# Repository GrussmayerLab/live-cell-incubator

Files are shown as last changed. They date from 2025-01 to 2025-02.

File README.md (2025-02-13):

This repository is created for an open-hardware project to develop a [live cell imaging incubator](https://grussmayerlab.github.io/live-cell-incubator/) by the KG group at TU Delft.

## Licensing and Attribution

This repository is licensed under the [MIT License]. You are generally free to reuse or extend upon this code as you see fit; just include the original copy of the license (which is preserved when you "make a template"). While it's not necessary, we'd love to hear from you if you do use this template, and how we can improve it for future use!

The deployment GitHub Actions workflow is heavily based on GitHub's mixed-party [starter workflows]. A copy of their MIT License is available in [actions/starter-workflows].

----

[MIT License]: https://en.wikipedia.org/wiki/MIT_License
[starter workflows]: https://github.com/actions/starter-workflows/blob/main/pages/jekyll.yml
[actions/starter-workflows]: https://github.com/actions/starter-workflows/blob/main/LICENSE

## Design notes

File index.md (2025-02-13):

---
title: Home
layout: home
---

# RM21Blanket - a live cell incubator 
 
Live cell experiments have become routine in the past decade or so and thus, a well-documented, (easy to adapt) open-source incubator design will be helpful to the life sciences community.

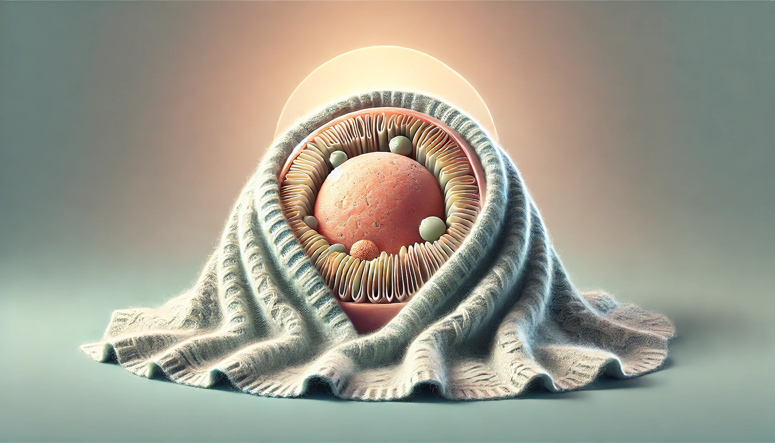
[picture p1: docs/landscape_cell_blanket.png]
A cell with a blanket alt >


In this project we have developed a live cell incubator with environmental controls for our home-built microscope based on the [RM21 platform by Mad City Labs](https://www.madcitylabs.com/rm21.html). This was the second iteration of our incubator chamber as the first version faced certain leakage and robustness issues. Our current design addresses these issues and incorporates several key features of an "ideal" incubator for live cell imaging:

1. Precise temperature control: Maintains a stable temperature, typically around 37°C for mammalian cells, with minimal fluctuations using commercial Oko Lab temperature control units.
2. Gas control: Accurate CO2 regulation (typically 5%) using Oko Lab CO2 control units, ensuring a consistent atmospheric environment.
3. Optimized flow dynamics: Careful consideration given to the flow and distribution of hot air and CO2 within the chamber for uniform environmental conditions.
4. Minimal evaporation and condensation: Use of closed ibidi dishes or sealed chambers significantly reduces these issues.
5. Compatibility: Designed for easy installation and compatibility with our home-built microscope setup.
6. Data logging: Utilizes Oko Lab control monitor for recording environmental parameters.
7. Multiple channel control: Ability to control temperature and CO2 parameters simultaneously for precise environmental regulation.
8. Minimal disturbance: Design allows for long-term imaging with minimal interference to the sample.
9. Design and Material choices: Black non-translucent PMMA material was chosen to fabricate the chamber based on its temperature tolerance, and also to avoid instances of stray light. The chamber has a door for easy mounting and access to the sample. Two sets of the door have been fabricated and can be easily interchanged- one with a transparent PMMA and one with the black non-translucent PMMA. For experiments involving microfluidic devices or specialized culture platforms, a transparent door allows researchers to easily check for issues like air bubbles, media evaporation, or unexpected cell behavior without compromising the experimental conditions.

While our current design doesn't include active humidity control or O2 regulation, the sealed environment and optimized flow dynamics help maintain stable conditions suitable for most standard cell culture experiments.

# Current State of the Project
Our live cell incubator project has successfully completed its second iteration, addressing leakage and robustness issues from the first version. 

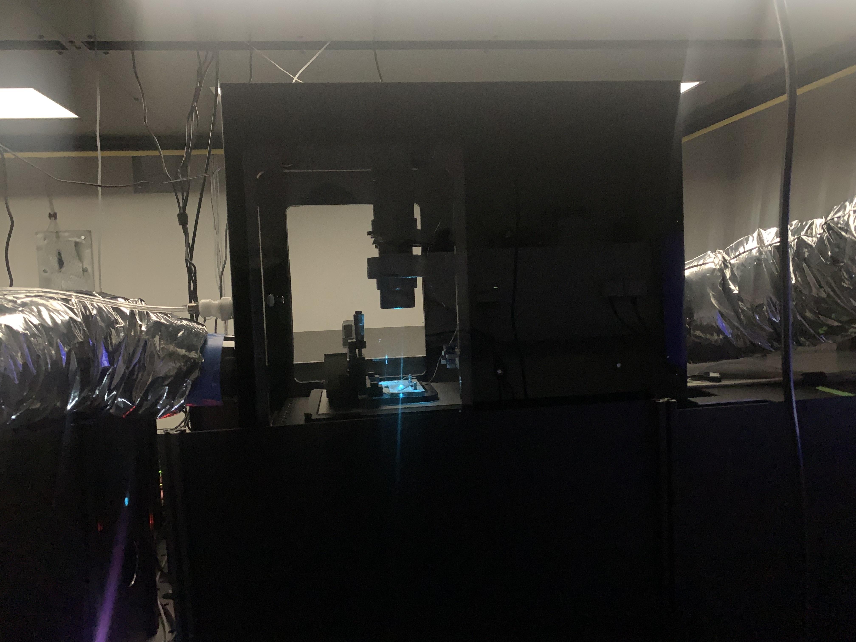
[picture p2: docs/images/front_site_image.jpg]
<br><br>

All the technical drawings, design files and bill of materials for the current version are available in the [project repo](https://github.com/GrussmayerLab/live-cell-incubator/). You can find the detailed [build instructions here]({{site.baseurl}}/build_instructions.html). Other than the mechanical parts listed in the BOM required to manufacture the chamber, you will also need:<br><br>

| Item| Quantity | Product Link| |
|----------|----------|---------|----|
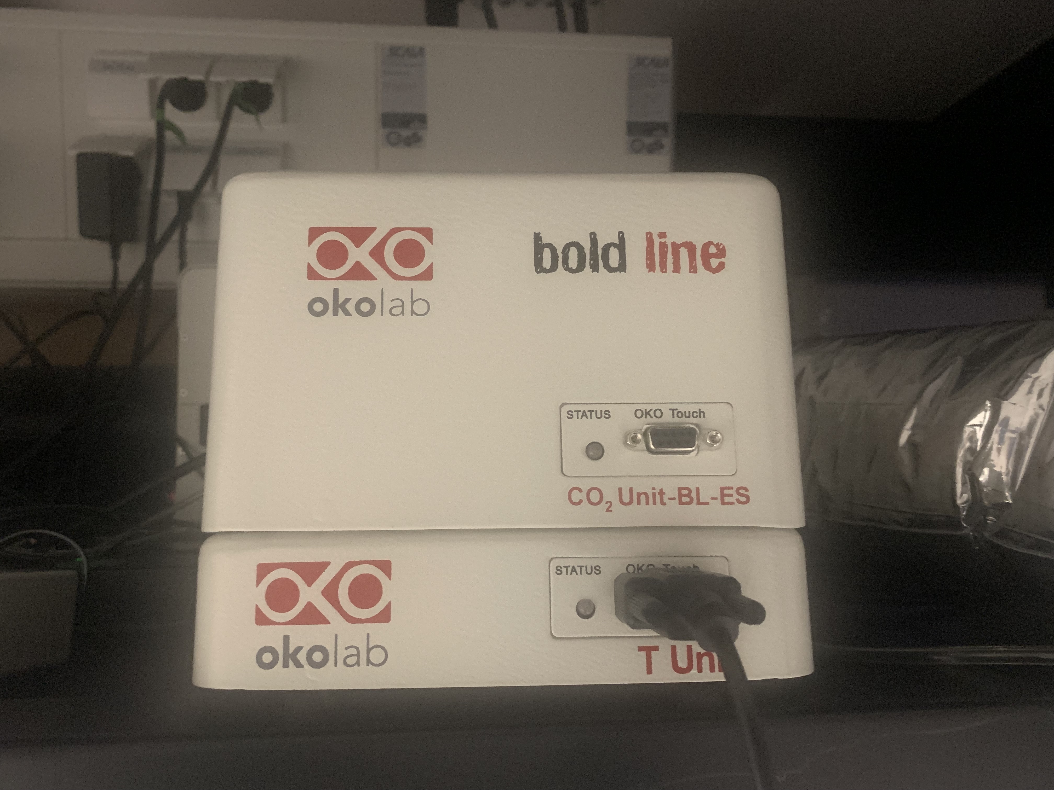
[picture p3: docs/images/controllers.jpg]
| Temperature control unit from Oko Lab with a chamber temperature sensor and a sample temperature sensor  | 1  | https://www.oko-lab.com/live-cell-imaging/cage-incubator/temperature-unit |   |
| CO2 control unit from Oko Lab  | 1   | https://www.oko-lab.com/gas-mixing/for-microscope-incubators/co2-unit-bl |  
| CO2 sensor   | 1  | | |
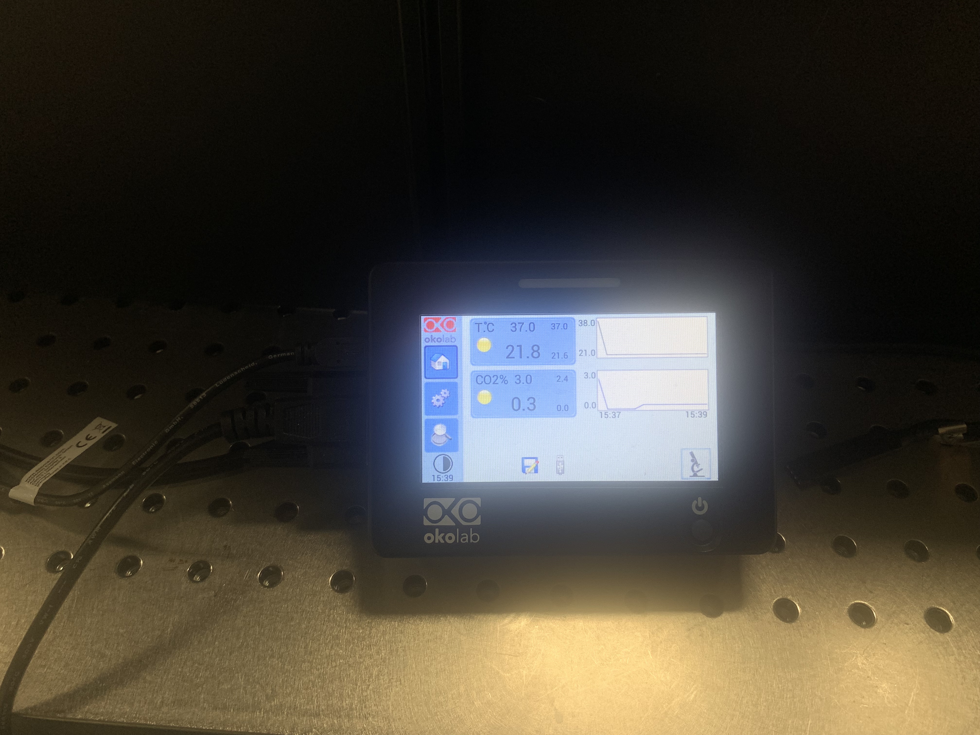
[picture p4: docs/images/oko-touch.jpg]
| Touch screen interface unit from Oko Lab  | 1  | https://okolab4microsystems.com/okolab_codes/oko-touch/ | 
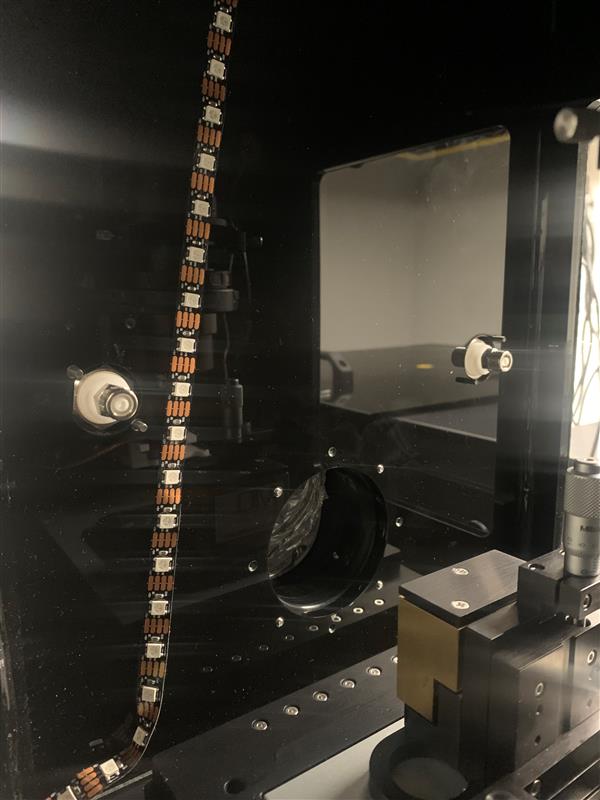
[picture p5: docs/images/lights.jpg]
| LED strip lights (optional)   | 1m  | Generic |  

# Testing and Validation
The incubator has been tested and is able to maintain contant temperature and CO2 levels for 4+ hours. We haven't tested extended durations yet as we do not currently image live cells for longer durations. A cell viability assay post imaging for 4 hours with the incubator resulted in only about 6-8% decline in viability.

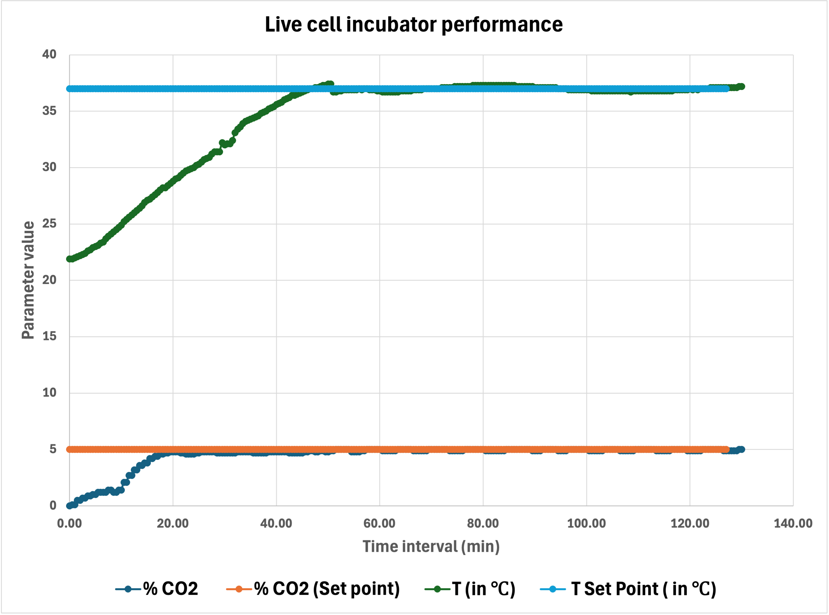
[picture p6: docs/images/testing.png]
<br><br>

# Future Plans
An active point of focus with respect to this design is to minimize environmental fluctuations while exchanging samples during imaging. The chamber door in our current design is relatively large which might mean everytime the door is opened, there could be sudden sharp fluctuations in the chamber equilibrium. In our testing, however, these effects weren't significant and the equilibrium is quickly maintained again. This could be because of the position of the gas inlet and outlet points with respect to the position of the door. Nevertheless, it is always advisable to go for a smaller door whenever possible. The incubator chamber can also be of a smaller footprint if it is designed just for fluorescence imaging and therefore, need not enclose the Koehler lamp as it does in the current design. 

Although not necessary at this point of time for our work, there is the option of exploring active humidity control for the incubator, if needed for specific experiments. This would also entail the issue of condensation which could potentially damage the optomechanics housed within the incubator chamber, so considerations have to be made accordingly. Additionally, for experiments requiring strictly hypoxic conditions, an active O2 control would be a good choice.

# Getting Started and Project Support
The information provided on this page should be sufficient for anyone looking to build a live cell incubator for imaging experiments for their microscope. Please report any questions or even suggestions you might have for us, using the "Issues" tab on our [github repo](https://github.com/GrussmayerLab/live-cell-incubator/issues) for this project. 

# License Information

# Special Thanks
This project was funded by the Open Hardware Stimulation Fund of the [Delft Open Hardware initiative](https://www.tudelft.nl/open-hardware/about-us). The chamber was designed by Frank Schilder and Moritz Engelhardt and developed by Frank, Moritz, and  Niek van Zon from TU Delft.

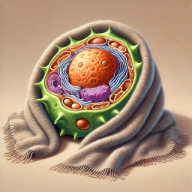
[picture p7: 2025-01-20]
docs/android-chrome-192x192.png

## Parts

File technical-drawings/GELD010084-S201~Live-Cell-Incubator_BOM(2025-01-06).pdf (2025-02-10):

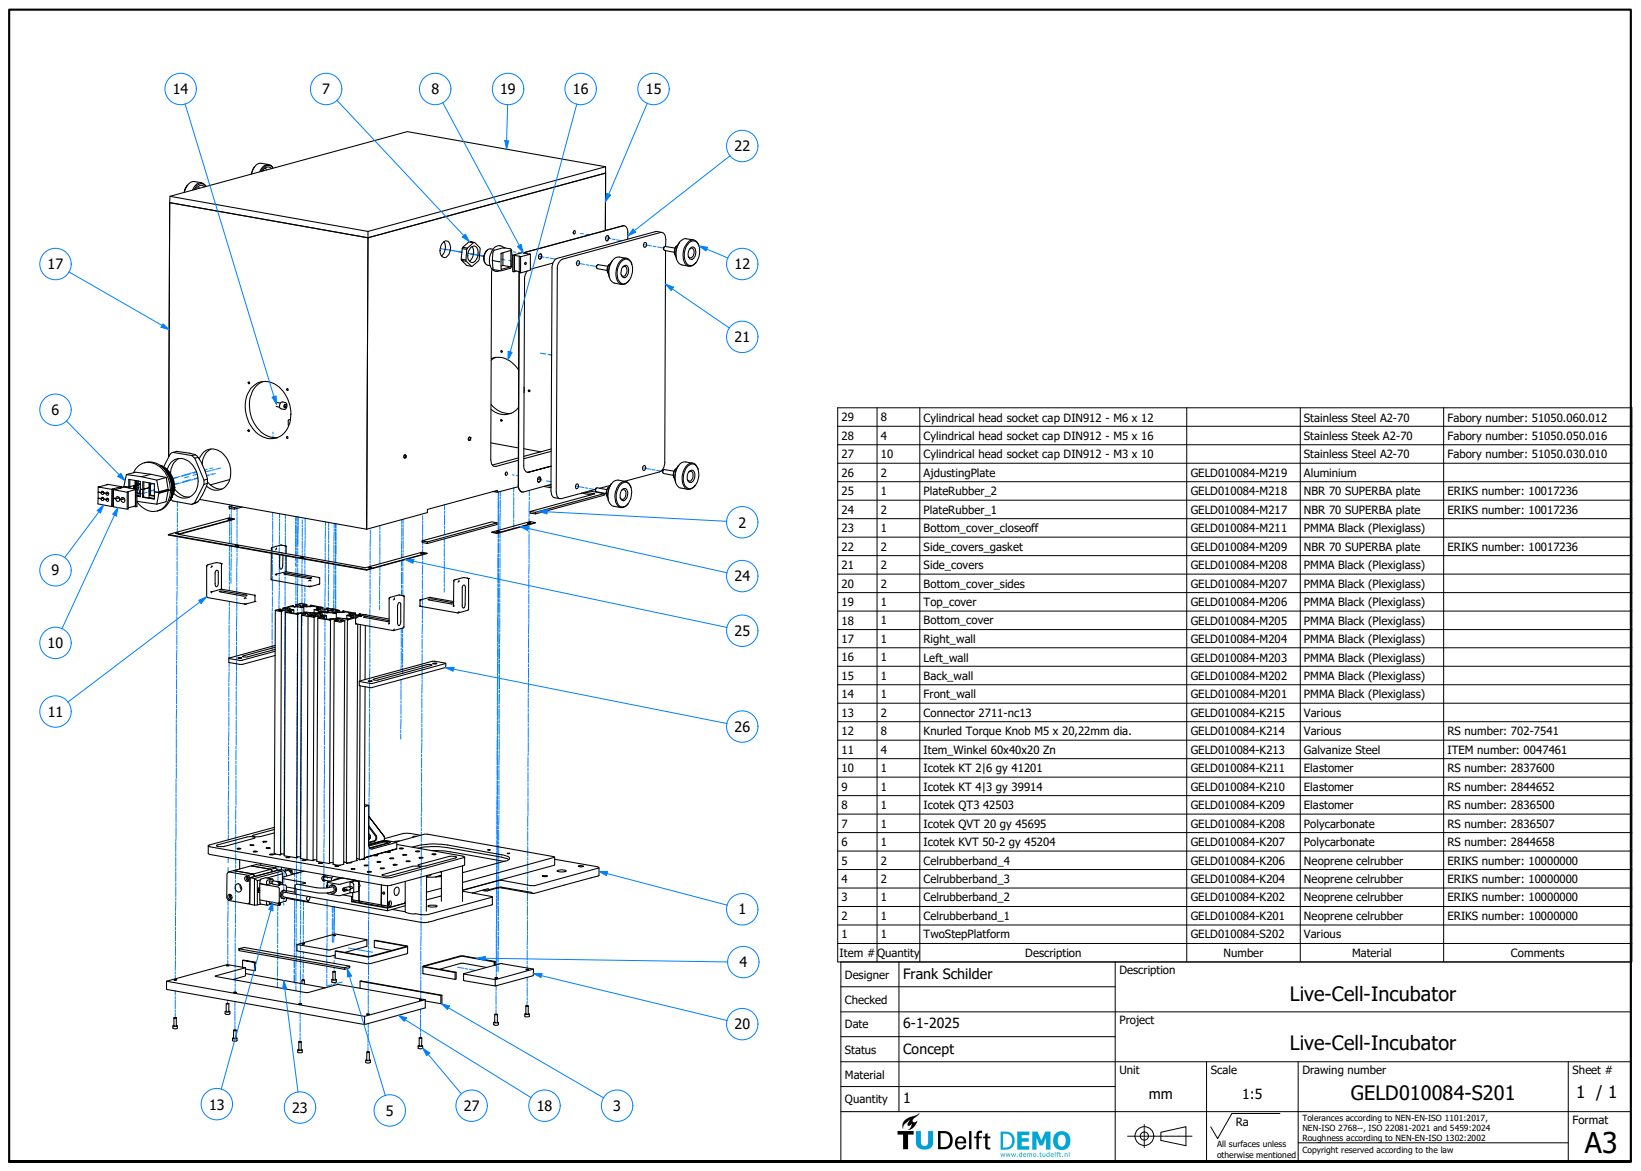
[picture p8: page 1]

29 | 8 | Cylindrical head socket cap DIN912 - M6 x 12 | | Stainless Steel A2-70 | Fabory number: 51050.060.012
28 | 4 | Cylindrical head socket cap DIN912 - M5 x 16 | | Stainless Steek A2-70 | Fabory number: 51050.050.016
27 | 10 | Cylindrical head socket cap DIN912 - M3 x 10 | | Stainless Steel A2-70 | Fabory number: 51050.030.010
26 | 2 | AjdustingPlate | GELD010084-M219 | Aluminium
25 | 1 | PlateRubber_2 | GELD010084-M218 | NBR 70 SUPERBA plate | ERIKS number: 10017236
24 | 2 | PlateRubber_1 | GELD010084-M217 | NBR 70 SUPERBA plate | ERIKS number: 10017236
23 | 1 | Bottom_cover_closeoff | GELD010084-M211 | PMMA Black (Plexiglass)
22 | 2 | Side_covers_gasket | GELD010084-M209 | NBR 70 SUPERBA plate | ERIKS number: 10017236
21 | 2 | Side_covers | GELD010084-M208 | PMMA Black (Plexiglass)
20 | 2 | Bottom_cover_sides | GELD010084-M207 | PMMA Black (Plexiglass)
19 | 1 | Top_cover | GELD010084-M206 | PMMA Black (Plexiglass)
18 | 1 | Bottom_cover | GELD010084-M205 | PMMA Black (Plexiglass)
17 | 1 | Right_wall | GELD010084-M204 | PMMA Black (Plexiglass)
16 | 1 | Left_wall | GELD010084-M203 | PMMA Black (Plexiglass)
15 | 1 | Back_wall | GELD010084-M202 | PMMA Black (Plexiglass)
14 | 1 | Front_wall | GELD010084-M201 | PMMA Black (Plexiglass)
13 | 2 | Connector 2711-nc13 | GELD010084-K215 | Various
12 | 8 | Knurled Torque Knob M5 x 20,22mm dia. | GELD010084-K214 | Various | RS number: 702-7541
11 | 4 | Item_Winkel 60x40x20 Zn | GELD010084-K213 | Galvanize Steel | ITEM number: 0047461
10 | 1 | Icotek KT 2|6 gy 41201 | GELD010084-K211 | Elastomer | RS number: 2837600
9 | 1 | Icotek KT 4|3 gy 39914 | GELD010084-K210 | Elastomer | RS number: 2844652
8 | 1 | Icotek QT3 42503 | GELD010084-K209 | Elastomer | RS number: 2836500
7 | 1 | Icotek QVT 20 gy 45695 | GELD010084-K208 | Polycarbonate | RS number: 2836507
6 | 1 | Icotek KVT 50-2 gy 45204 | GELD010084-K207 | Polycarbonate | RS number: 2844658
5 | 2 | Celrubberband_4 | GELD010084-K206 | Neoprene celrubber | ERIKS number: 10000000
4 | 2 | Celrubberband_3 | GELD010084-K204 | Neoprene celrubber | ERIKS number: 10000000
3 | 1 | Celrubberband_2 | GELD010084-K202 | Neoprene celrubber | ERIKS number: 10000000
2 | 1 | Celrubberband_1 | GELD010084-K201 | Neoprene celrubber | ERIKS number: 10000000
1 | 1 | TwoStepPlatform | GELD010084-S202 | Various
Item # Quantity | | Description | Number | Material | Comments
Designer | Frank Schilder | Description Live-Cell-Incubator

Checked
Date | 6-1-2025 | Project Live-Cell-Incubator

Status | Concept

Material | | Unit mm | Scale 1:5 | Drawing number GELD010084-S201 | Sheet # 1 / 1

Quantity | 1

Ra All surfaces unless otherwise mentioned | Tolerances according to NEN-EN-ISO 1101:2017, NEN-ISO 2768--, ISO 22081-2021 and 5459:2024 Roughness according to NEN-EN-ISO 1302:2002 | Format A3

Copyright reserved according to the law

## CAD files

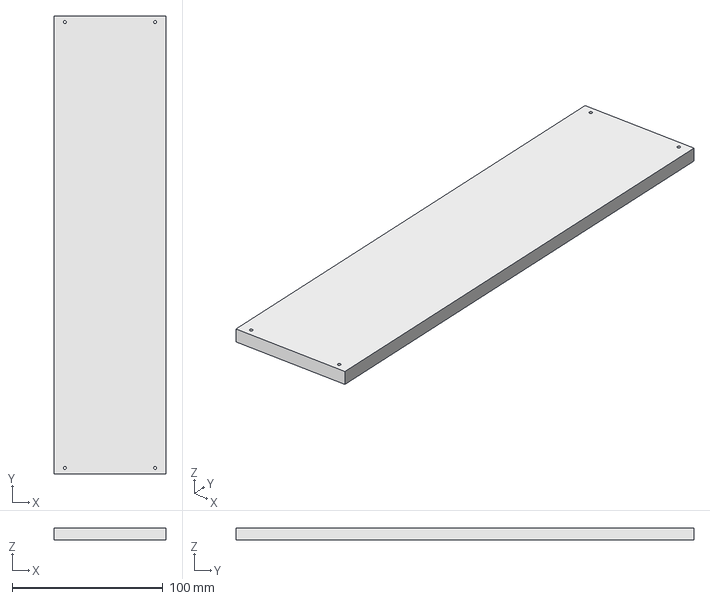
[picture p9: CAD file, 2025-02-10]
technical-drawings/GELD010084-M215~Drill_guide1(2024-12-31).stp
74.2 x 304.1 x 8.00 mm

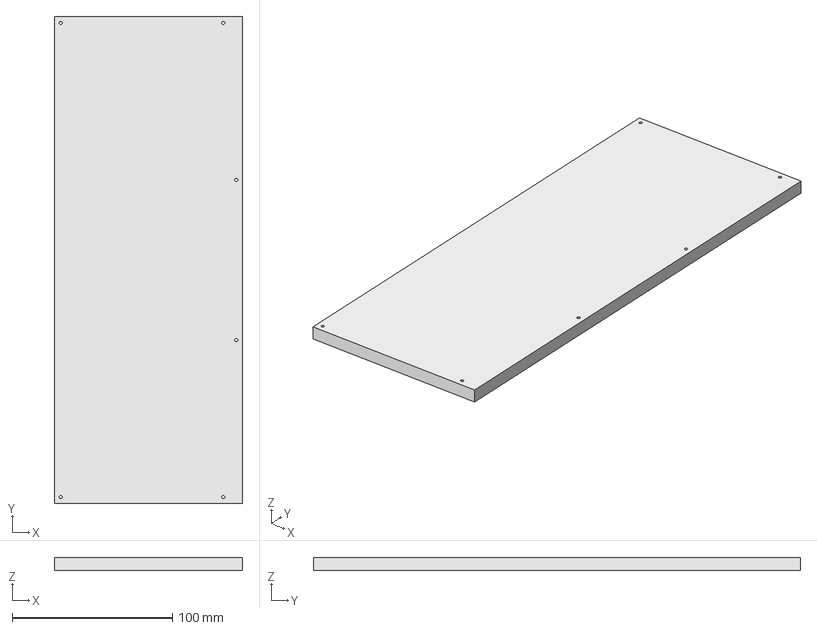
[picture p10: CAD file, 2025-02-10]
technical-drawings/GELD010084-M216~Drill_guide2(2024-12-31).stp
117.7 x 304.1 x 8.00 mm

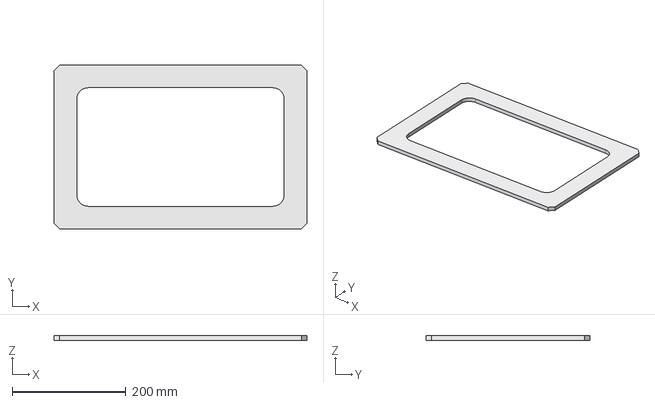
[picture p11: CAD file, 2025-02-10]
technical-drawings/GELD010084-M214~Glue-framing(2024-12-31).stp
444.0 x 288.0 x 8.00 mm

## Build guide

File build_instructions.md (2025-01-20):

---
title: Build instructions
layout: home
---

# Live Cell Incubator
In the current setup there already is an incubator used. In the current incubator there are many openings for gas to escape and the material is wearing down (bending). The main aim for the new incubator is making it airtight as much as possible. The materials used should withstand 37°C and CO² gas.

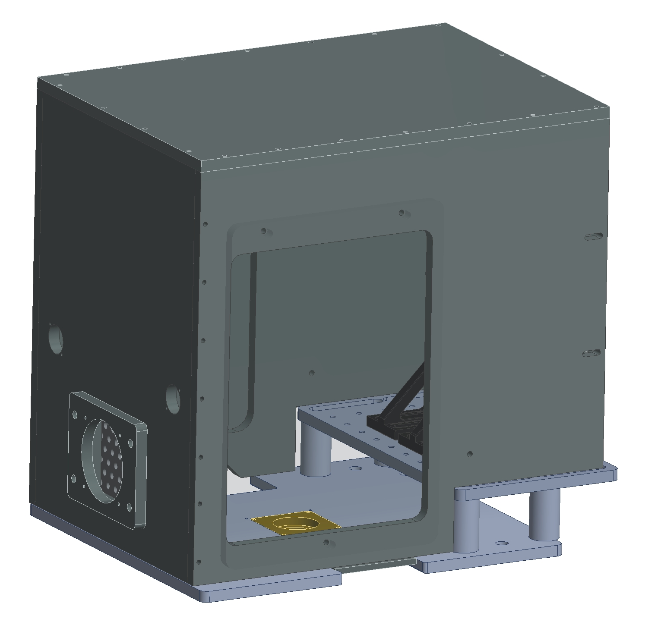
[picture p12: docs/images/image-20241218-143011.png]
The old incubator


The connectors of the old incubator will be used in the new incubator and the dimensions will be taken as a guide to draw up the new version. The old incubator is made of loose panels that will be bolted together. The old incubator is placed loosely on the platform. There are big openings to allow cables passing through. 
# Design  
The incubator has to fit on a platform that has two levels. On the top level a column is mounted which has the microscope attached to it. The old incubator sat on top of both levels of the platform, which left gaps between the top and bottom level. The new incubator will sit only on the bottom level en go over the second level completely. 

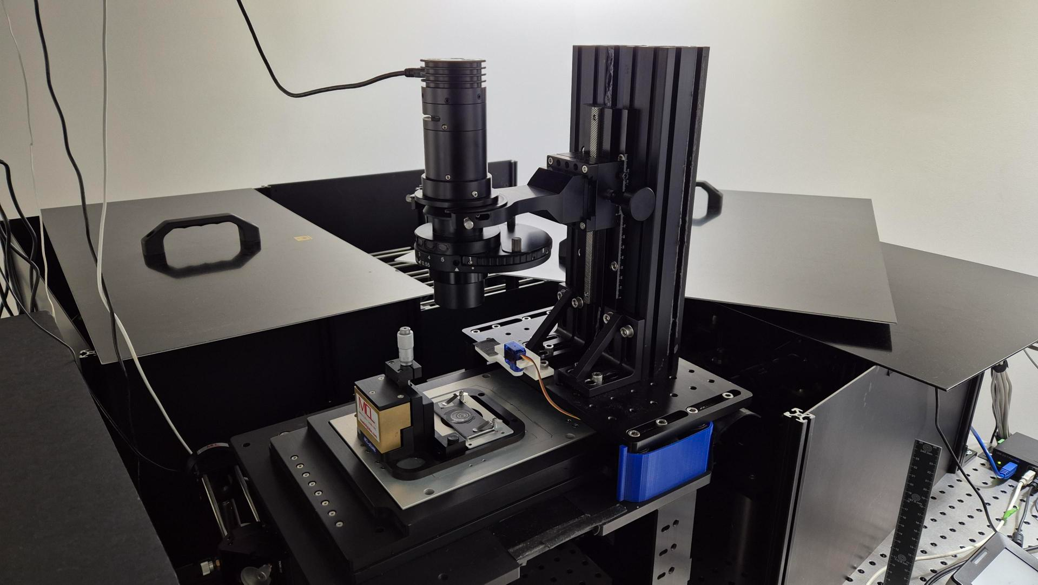
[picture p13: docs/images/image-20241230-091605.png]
The platform without the incubator with the microscope


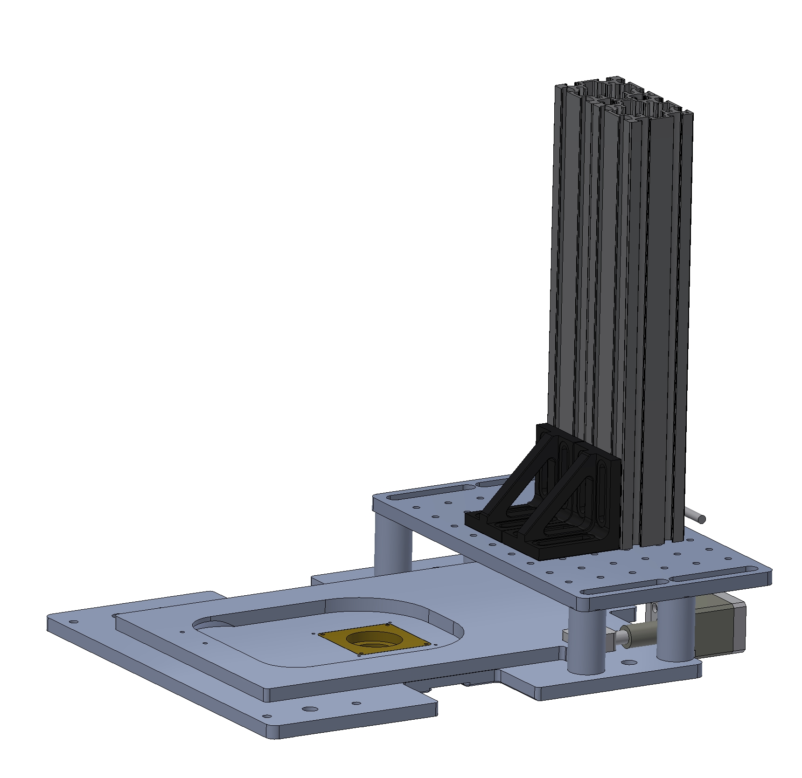
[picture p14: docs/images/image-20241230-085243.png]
CAD view of the platform


The new incubator will also consist of loose panels but now glued together as much as possible. The edge of the incubator will be covered with a neoprene foam strip to create a seal between the incubator and the platform. The cables will go through a cable gland. The panels of the incubator are made of black non-translucent PMMA (acrylic). The black PMMA does not let light through. 

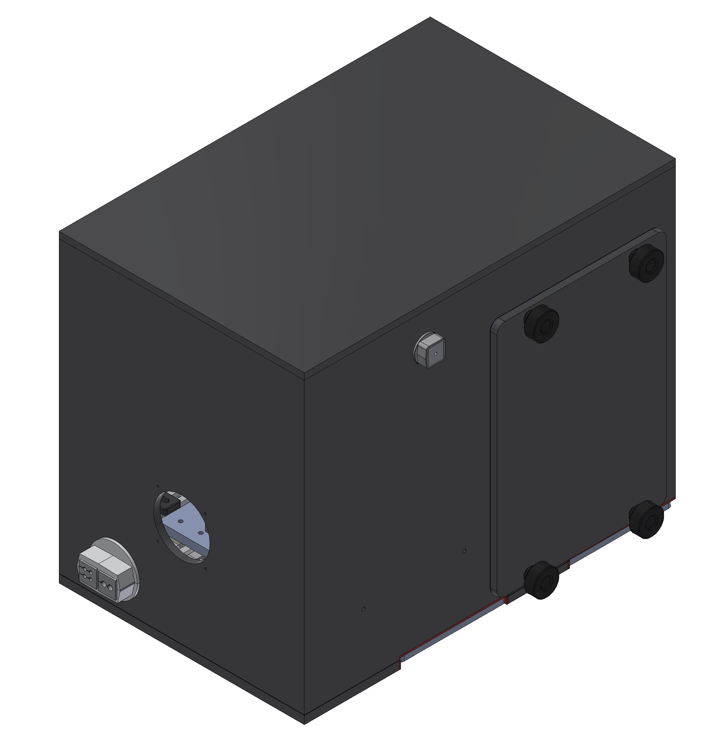
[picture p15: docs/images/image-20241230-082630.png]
Isometric view of the incubator


There are two ø6mm cables and four ø3mm cables coming from the right side and one ø4mm cable on the back. To let out the cables as airtight as possible the cable glands from the brand Icotek where used. These cable gland can be used without removing the connector.  

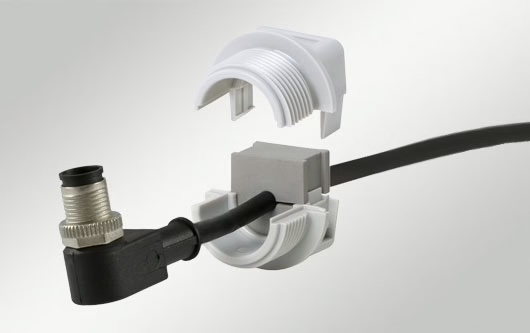
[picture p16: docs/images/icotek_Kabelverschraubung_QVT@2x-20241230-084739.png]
Icotek cable gland


- Due to availability the IP54 versions where used, a better air-tightness is to be expected with the IP68 version. 
- During the installation there was an second cable that had to go out at the back. This cable is squeezed with the ø4mm cable in the cable gland. 

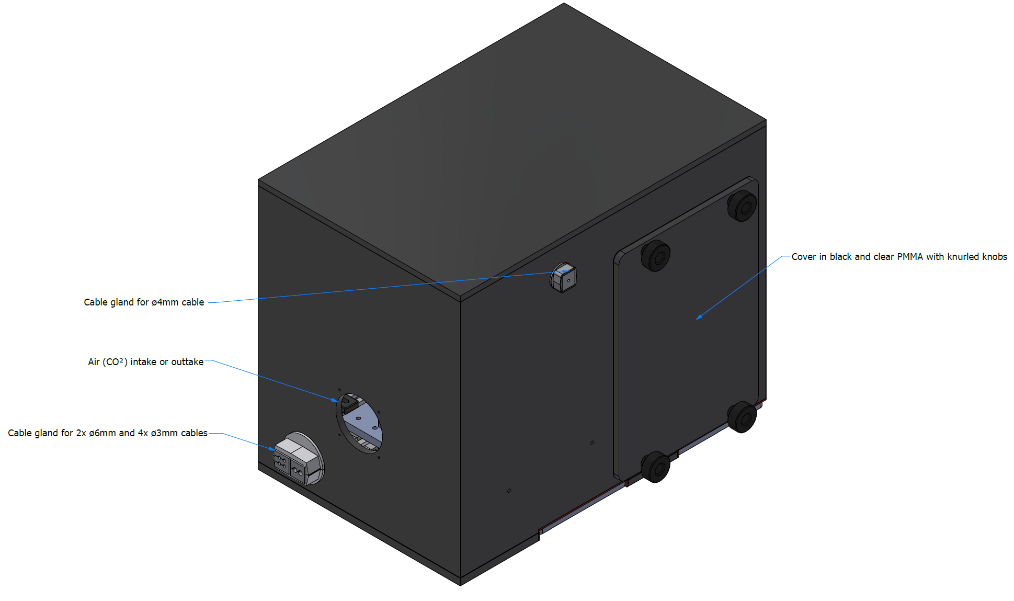
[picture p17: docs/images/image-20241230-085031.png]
Isometric view of the back with the grommets


The four side panels and the top panel are glued together with ANGLOSOL CEMENT 700 (two part acrylic
adhesive) together. This will create a strong airtight bond. Between the side covers and the incubator is a rubber gasket (the gasket is glued to the incubator).  
After placing the incubator on the platform the tree bottom panels can be mounted and then bolted down with M3 bolts. Between the connecting surfaces of the panels and the incubators is a rubber gasket (the gasket is glued to the incubator). 
All edges of the incubator that make contact with the platform are covered with a foam rubber strip. 

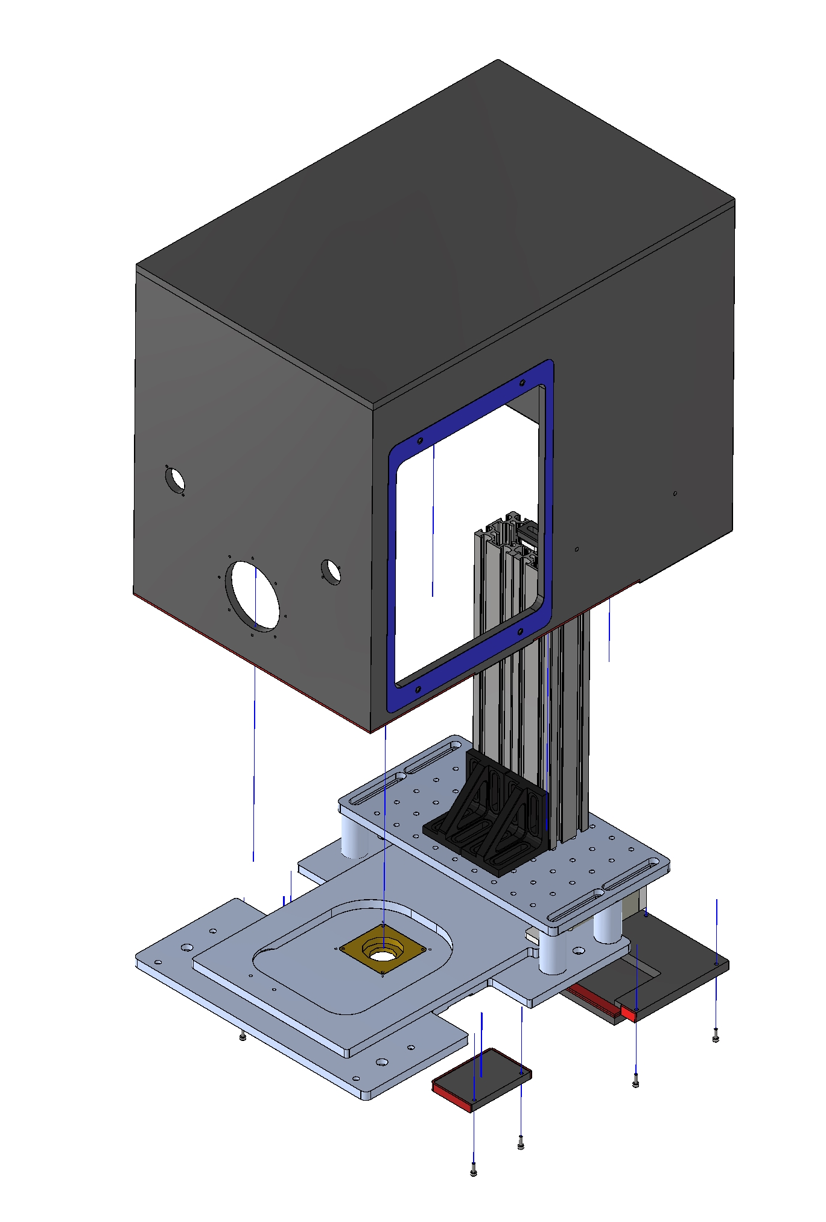
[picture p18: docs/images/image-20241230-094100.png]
Assembly on the stage platform


The incubator is secured to the second level of the platform by angle brackets. An extra strip is added to created a adjustable mounting position to fit alignment issues.  

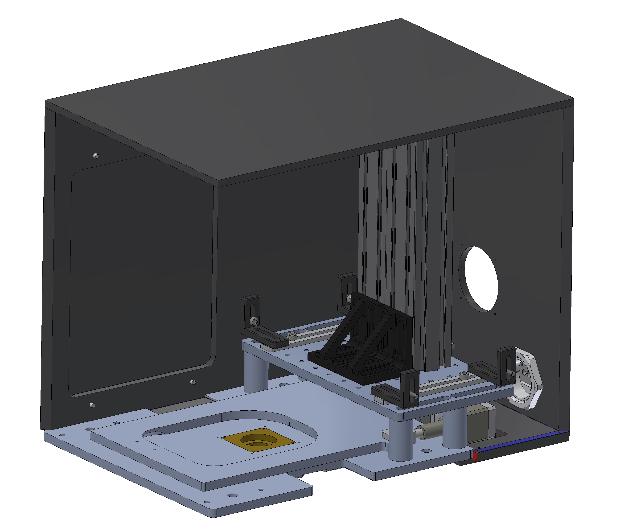
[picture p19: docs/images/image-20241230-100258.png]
Inside view of mounted chamber


# Parts To Order 
The cable glands and knurled knobs can be orders at RS-Components, the rubber gasket and rubber foam can be ordered at ERIKS, the bracket can be ordered at ITEM, bolts at FABORY and the 8mm black PMMA can be ordered at Vink-Kunststoffen.     

| Part      | Quantity | Part number    | Product Link  |
|---------- |----------|---------       |----           | 
| RS-COMPONENTS | | | | 
| Icotek Grey Elastomer Cable Grommet KT 2/6 | 1  | 283-7600 | [Link](https://nl.rs-online.com/web/p/cable-grommets/2837600) | 
| Icotek Grey Elastomer 888mm Cable Grommet KT 4/3 | 1 | 284-4652 | [Link](https://nl.rs-online.com/web/p/cable-grommets/2844652) | 
| Icotek Polycarbonate Cable Trunking Frame, 66 x 66 x 37mm, KVT | 1 | 284-4658 | [Link](https://nl.rs-online.com/web/p/cable-trunking-accessories/2844658) | 
| Icotek QVT Series Grey Polycarbonate Cable Gland, M20 Thread, IP54 | 1 | 283-6507 | [Link](https://nl.rs-online.com/web/p/cable-glands/2836507) | 
| Icotek Grey Elastomer Cable Grommet QT 3 | 1 | 283-6500 | [Link](https://nl.rs-online.com/web/p/cable-grommets/2836500) | 
| Knurled Torque Knob M5 x 20,22mm dia | 10 | 702-7541 | [Link](https://nl.rs-online.com/web/p/clamping-knobs/7027541) | 
| ITEM | | | | 
| Winkel 60x40x20 Zn, schwarz | 4 | 47461 | [Link](https://www.item24.com/en-de/bracket-60x40x20-zn-black-47461) | 
| ERIKS | | | | 
| Prof.CR FEST cel-zelfkl zwart 10x2 L=20 | 20 | | [Link](https://shop.eriks.nl/nl/rubber-producten-rubber-profielen/strip-celrubber-zelfklevend-cr-fest-zwart-10x2-l-20m-10000000/) | 
| Plaat SUPERBA 1400x0,5 | 1 | 10017236 | [Link](https://shop.eriks.nl/nl/rubber-plaat-nbr-70-superba-20000x1400x0-5-10017236/) | 
| Vink-Kunststoffen | | | | 
| Altuglas PMMA Plaat Gegoten Zwart 101 48000 3050x2030x8mm | | 107859 | [Link](https://www.vinkkunststoffen.nl/altuglas-pmma-plaat-gegoten-zwart-101-48000-3050x2030x8mm?queryID=4f88efcd48d9f4c89b59187c54d6eb02&objectID=143940&indexName=prod_vink_kunststoffen_nl_products) | 
| FABORY | | | | 
| Hexagon socket head cap screw DIN 912 Stainless steel A2 M3X10 | 10 | 51.050.030.010 | [Link](https://www.fabory.com/en_NL/hexagon-socket-head-cap-screw-din-912-stainless-steel-a2-m3x10/p/51050030010?q=m3x10+912din%3Arelevance%3AFA5500%3AStainless%2Bsteel&amp;searchQuery=m3x10%20912din) | 
| Hexagon socket head cap screw DIN 912 Stainless steel A2 M5X16 | 4 | 51.050.050.016 | [Link](https://www.fabory.com/en_NL/hexagon-socket-head-cap-screw-din-912-stainless-steel-a2-m5x16/p/51050050016?q=%3Amost-popular%3AFA5500%3AStainless%2Bsteel%3AFA5184%3A16%2Bmm%3AFA3094%3AM5) | 
| Hexagon socket head cap screw DIN 912 Stainless steel A2 M6X12 | 8 | 51.050.060.012 | [Link](https://www.fabory.com/en_NL/hexagon-socket-head-cap-screw-din-912-stainless-steel-a2-m6x16/p/51050060012?q=%3Amost-popular%3AFA5159%3ADIN%2B912%3AFA3094%3AM6%3AFA5184%3A16%2Bmm%3AFA5500%3AStainless%2Bsteel) | 

# Manufacturing 

Inside view of mounted chamber

All the PMMA plates are laser cut on the TROTEC Speedy 400. 2D outlines of the parts are exported as DXF files. The laser cutter cuts on the line of the dxf. This means that there is no offset compensation in the software. Dimensions of the dxf are adjusted to accommodate for the offset.  
Parts cut on the laser cutting machine

Before gluing the panels the M3 and M5 helicoil thread inserts are placed. The thread holes were kept smaller when cut. The holes for the threads are drilled to the correct size (M3=ø3,1, M5=ø5,2) using the smaller cut holes to position. Then the threads are tapped with the helicoil tap M3 and M5 and the helicoil are inserted.
Parts M205 and M211 need to be countersunk for cylindrical M3 bolt heads.    
The sides of parts M201 till M204 needs to have a +- 43 degree angle. Two 45° edges will make a 90° corner. With gluing the missing 2°/4° will be filled. The angles are cut on a table saw with the blade angled.     

Sides cut on an angle

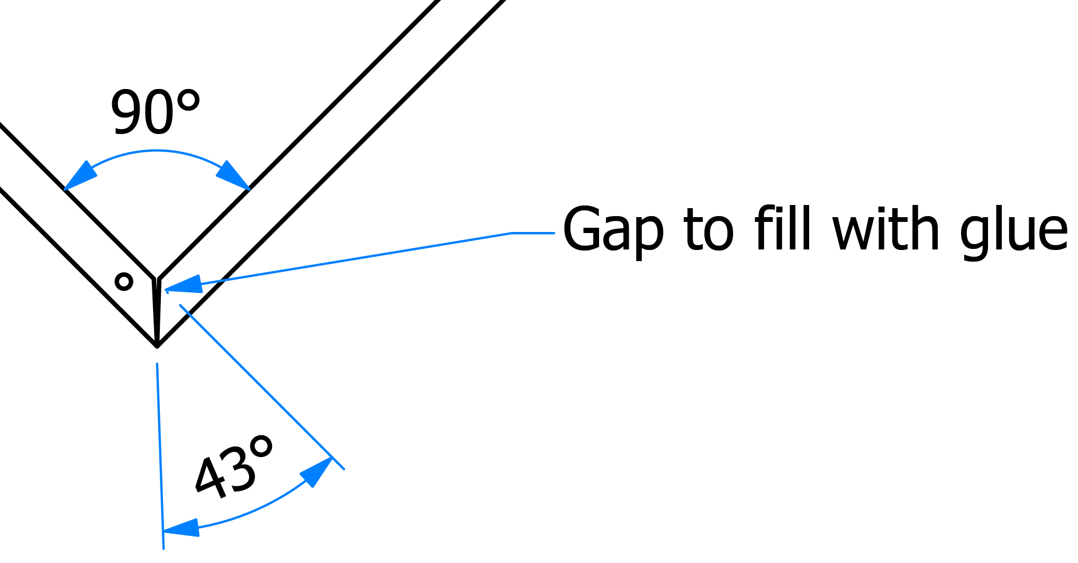
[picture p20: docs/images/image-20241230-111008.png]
Gap for gluing


To ensure a proper alignment with gluing two gluing molds are used. These are two plates that have the dimensions of the inside of the box. 

- The gluing molds should determine the dimensions of the incubator when gluing. Measure the gluing molds outer dimension to be sure that the dimensions are correct. 

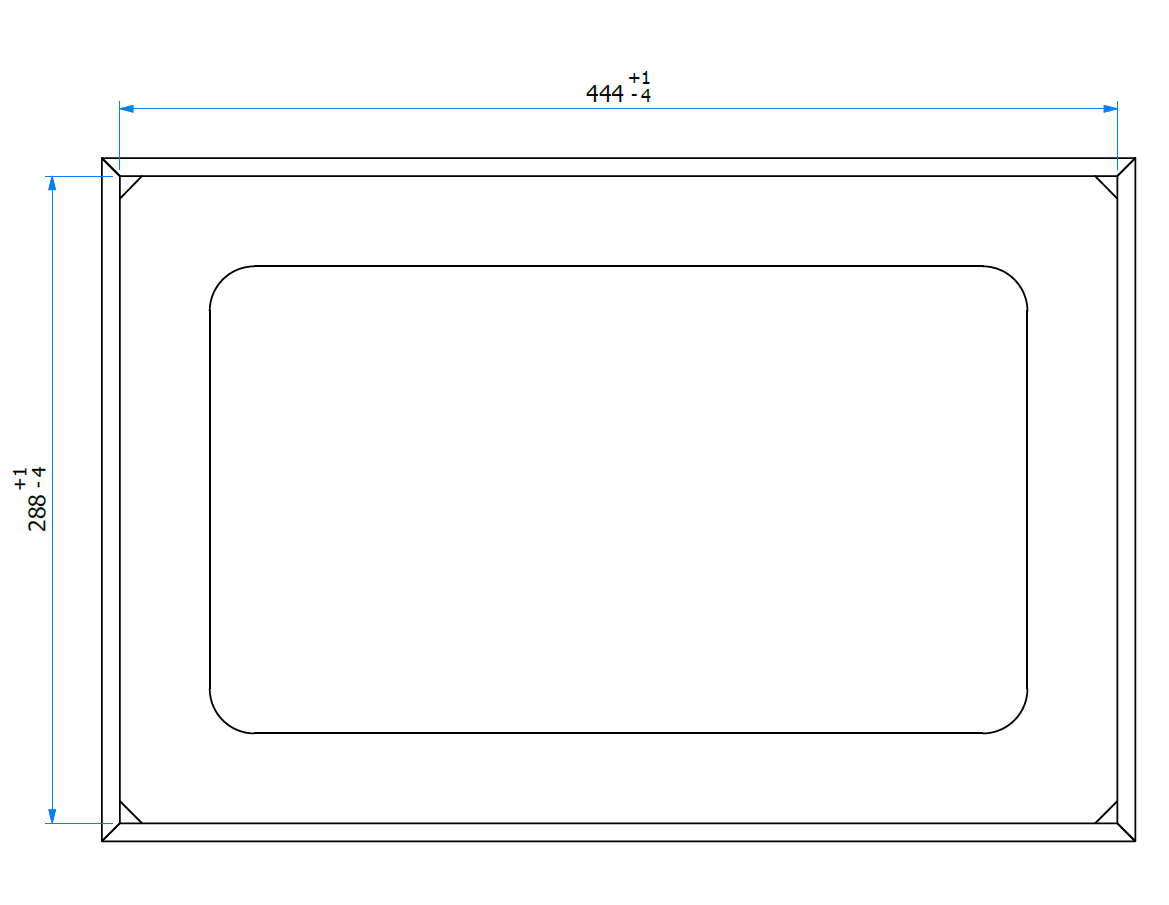
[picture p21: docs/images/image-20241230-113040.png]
Tolerance of the gluing mold (top view)


Two corresponding adjacent panels are placed next to each other and taped together on the long side. When taped the two panels can be placed in a 90° angle. This is also done with the other two panels. These two sets of panels can be placed together and checked with the gluing mold. 

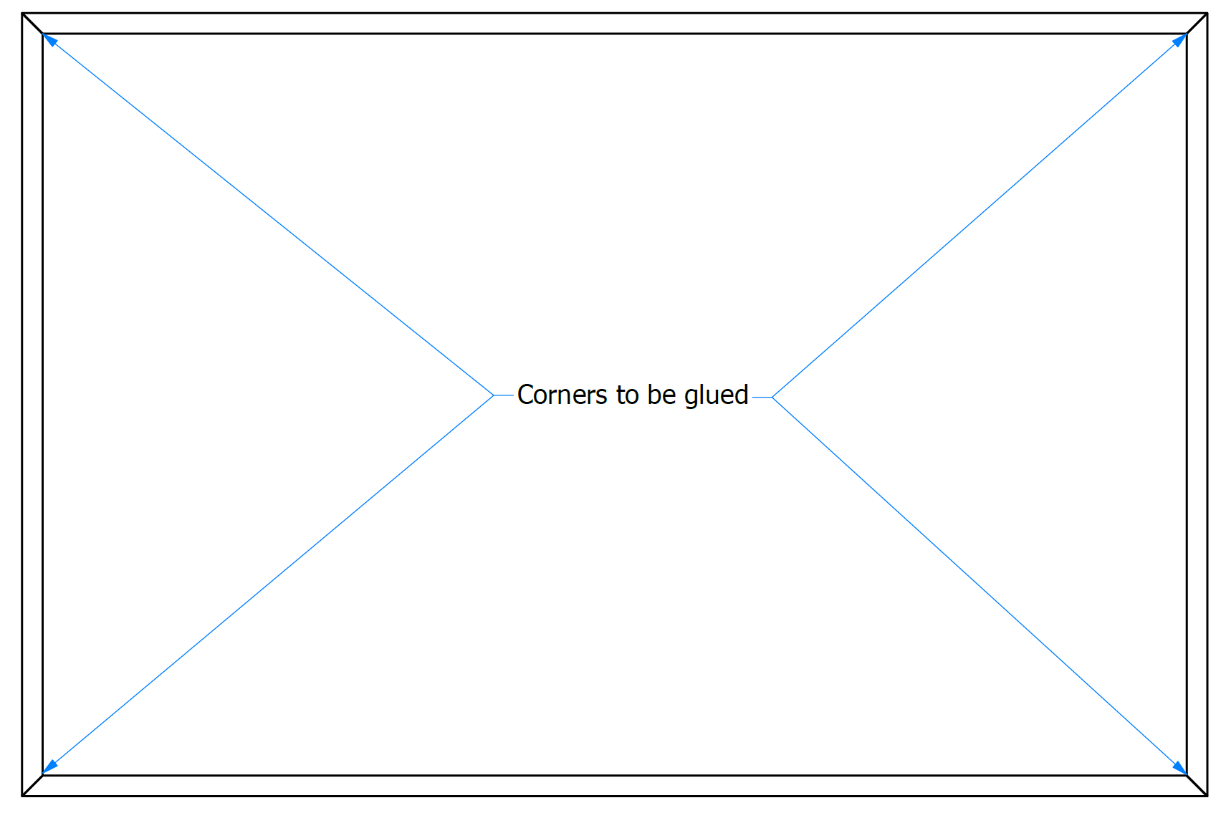
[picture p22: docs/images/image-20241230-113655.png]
Corners that need to be glued (top view)


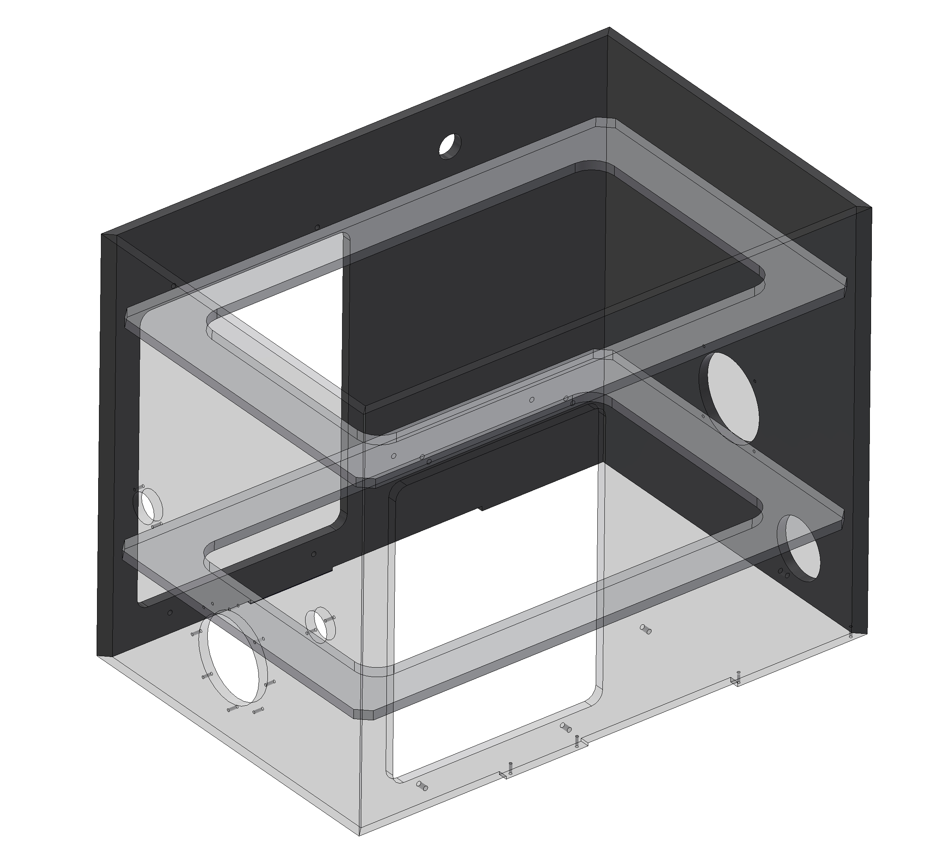
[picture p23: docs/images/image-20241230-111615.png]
View of gluing mold fitted inside of the panels

    
The panels will be glued in an 90° angle block, corner by corner. The side of the corners are taped off so the glue doesn’t run out between the plates, also on the ends of the plate. The corner of the first set of panels is then filled with glue and let to dry. This is repeated for the second set of panels.
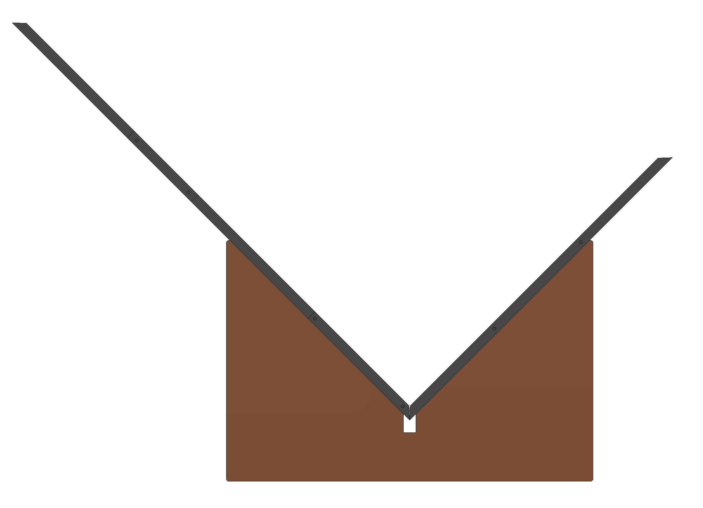
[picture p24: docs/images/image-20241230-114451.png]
One set of panels ready to be filled with glue


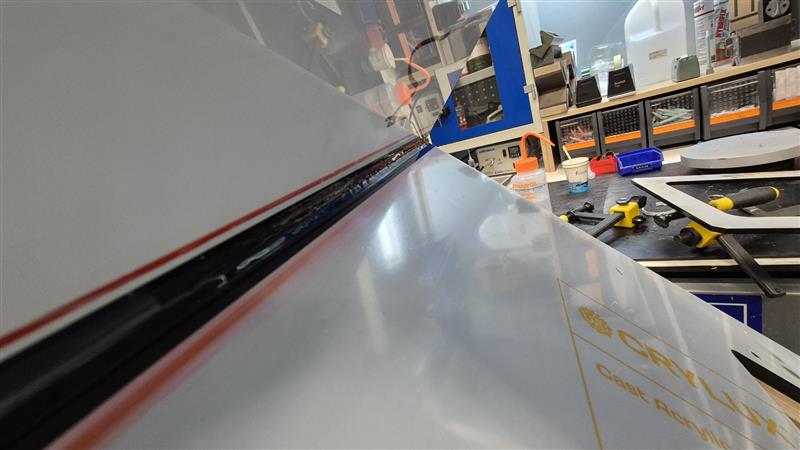
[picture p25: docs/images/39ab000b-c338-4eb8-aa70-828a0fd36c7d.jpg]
Corner filled with glue

   
In the angle block together with the gluing mold the remaining corners can be glued. 
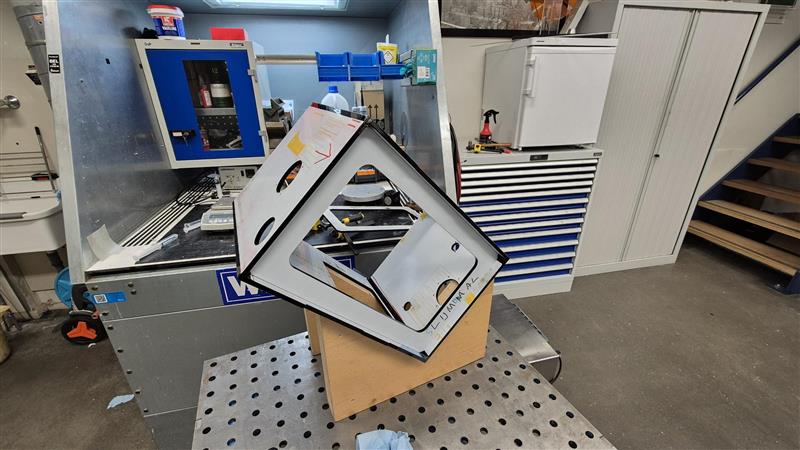
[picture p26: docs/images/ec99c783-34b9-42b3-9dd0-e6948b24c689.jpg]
Glued corners with the gluing mold and angle block


After gluing any overflowing glue needs to be removed. 
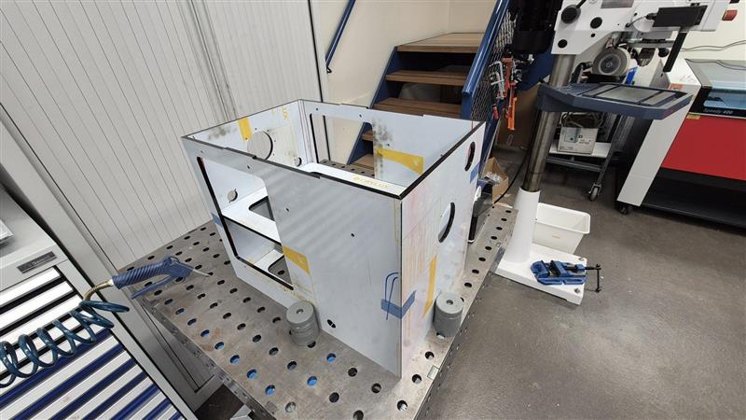
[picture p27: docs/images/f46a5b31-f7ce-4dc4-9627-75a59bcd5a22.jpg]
The incubator without the top panel

    
After gluing all the side panels the top panel can be glued. An even layer of glue is put on the top edge of the panels and the top panel is placed on top it. 
When all panels are glued together the holes on the bottom of the incubator are drilled (ø3,1mm) for M3 Helicoil thread inserts using two drill guides. The drill guides are aligned and clamped to the bottom of the incubator and the holes are drilled through the guides. Then the thread inserts are placed.
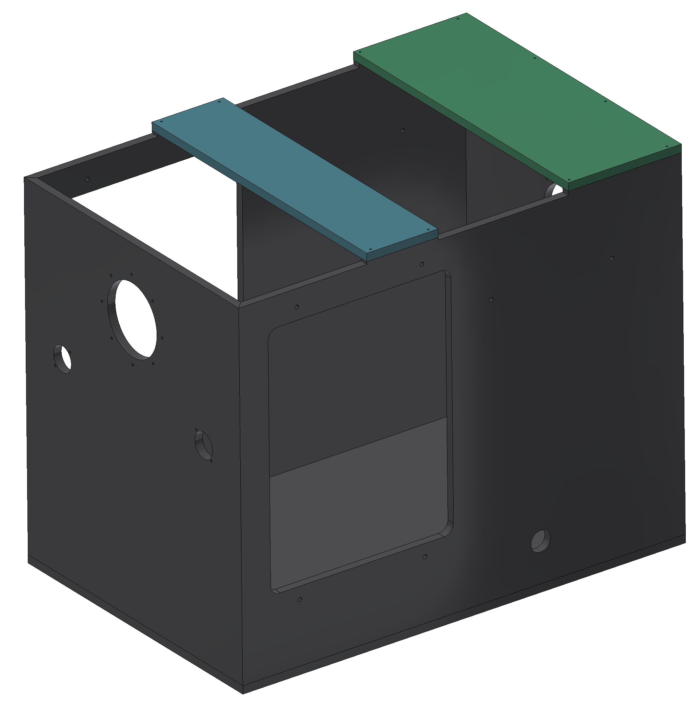
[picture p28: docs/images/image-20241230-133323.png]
Drill guides (blue and green)

    
The right bottom panel consists of two plates that need to be glued together.
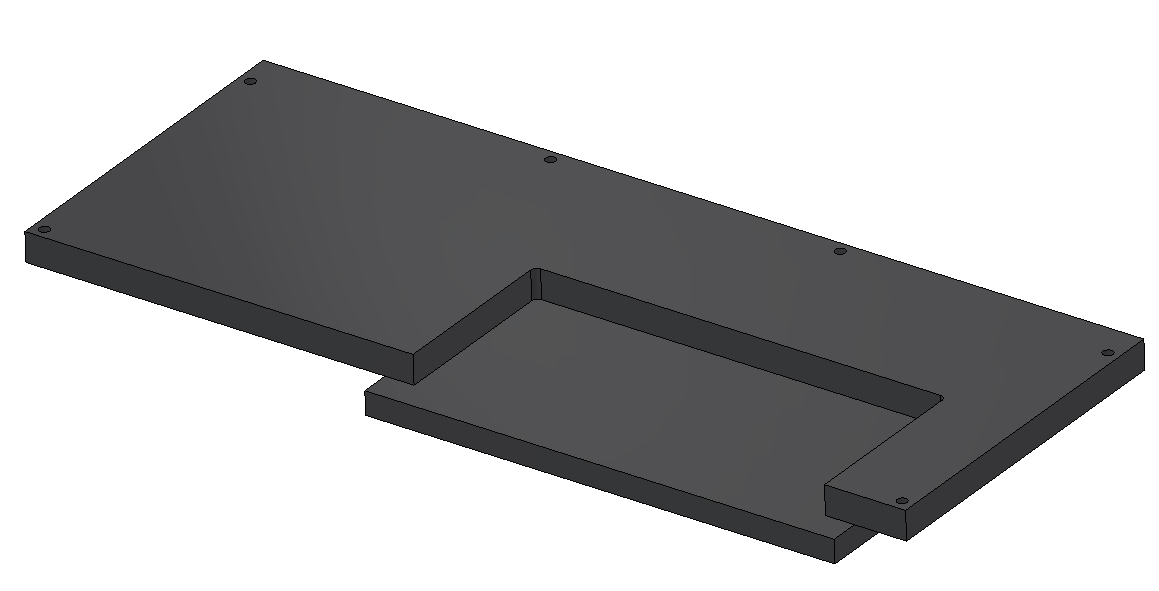
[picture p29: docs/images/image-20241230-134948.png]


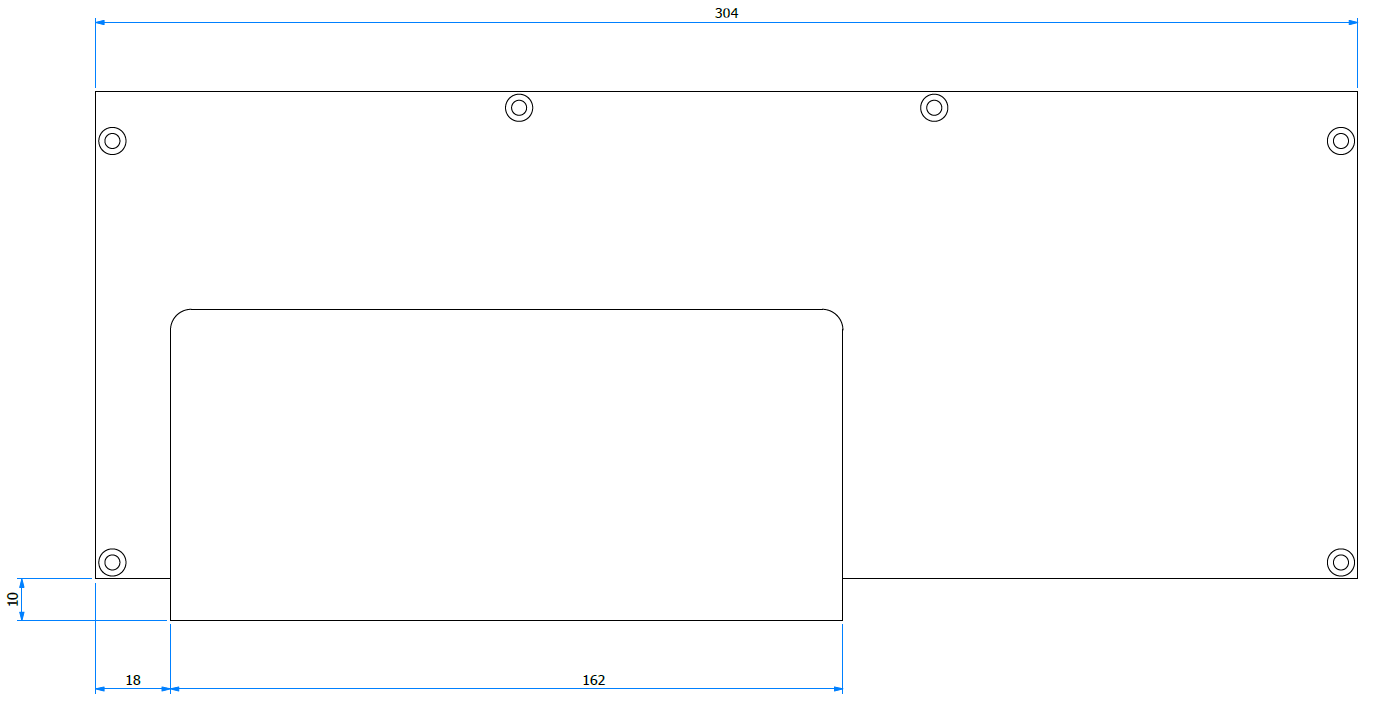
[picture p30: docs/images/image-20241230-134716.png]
![]

 - Afterwards part M205 is made of 10mm thick plate instead of 8mm like the rest of the panels for extra clearance when installing. 

The rubber gaskets between the bolted parts are cut out of a NBR rubber plate using a water-jet cutting machine (cut with only water, no abrasive). The gaskets are glued to the incubator using Cyanolit.

- Instead of gluing the gasket, a gasket with on one side sticky tape can be used. Due to availability the standard sheet is used.  

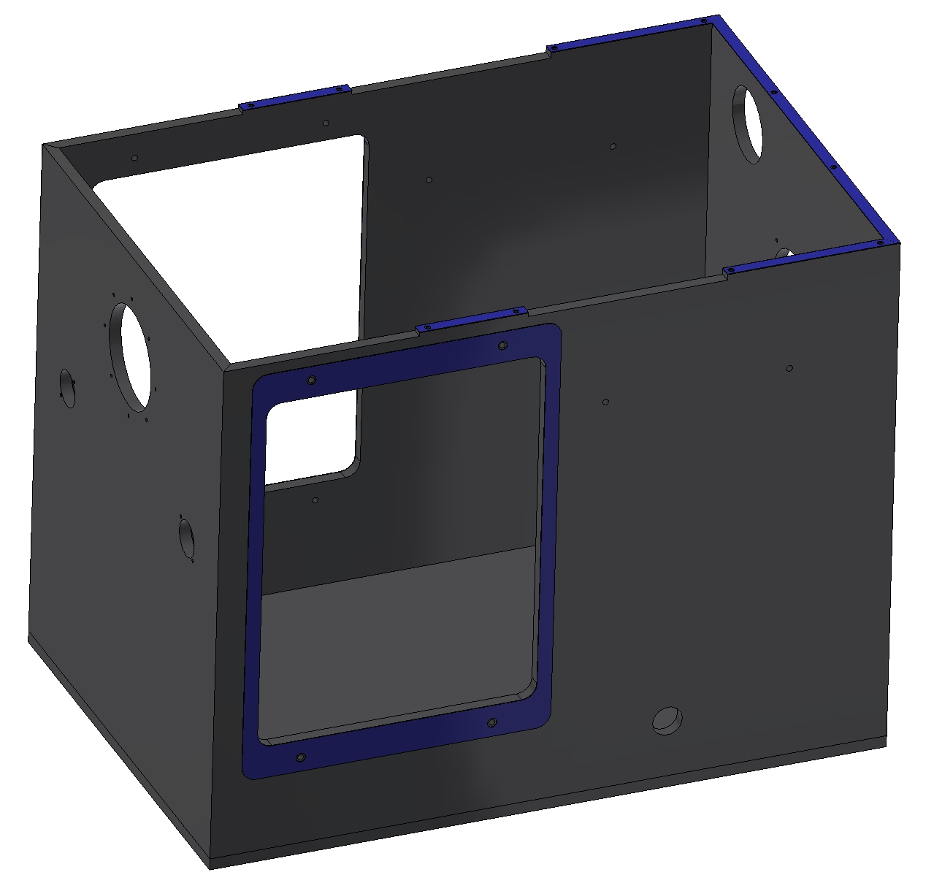
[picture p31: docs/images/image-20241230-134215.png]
Incubator with gaskets (blue) glued


Then the 2mm foam rubber is put on the bottom edges of the incubator. The foam rubber is sticky on one side. The foam rubber is put on the edge and cut to length with a sharp knife.
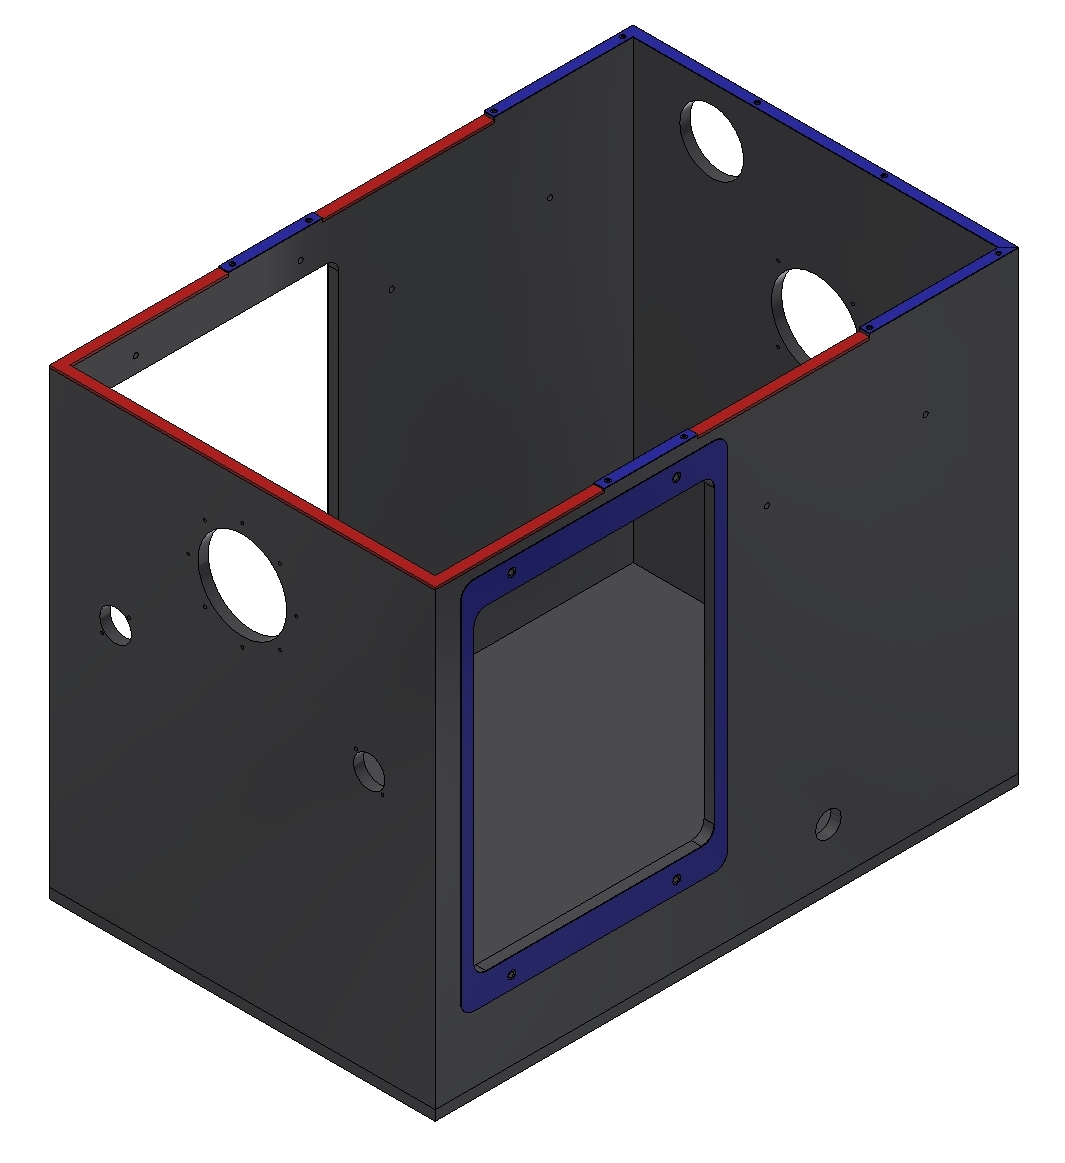
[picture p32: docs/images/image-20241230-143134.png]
Incubator with foam rubber (red)

    
The foam rubber is also placed on the bottom covers. To accommodate for the 10mm plate two strips of 2mm foam are placed on top of each other on the flat panel.
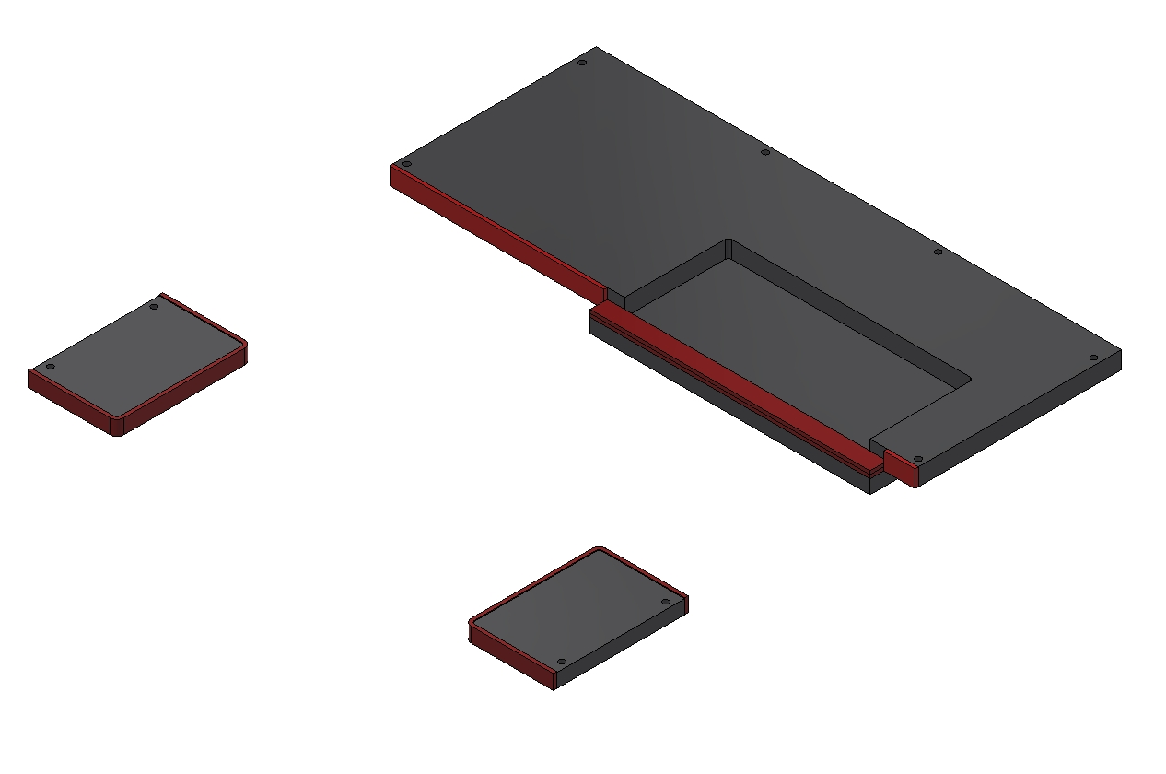
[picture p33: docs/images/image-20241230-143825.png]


# Assembly 
First the angle brackets and adjuster plate are mounted to the inside of the incubator. The bolts aren’t tightened completely so it can be move in position when placed on the platform.
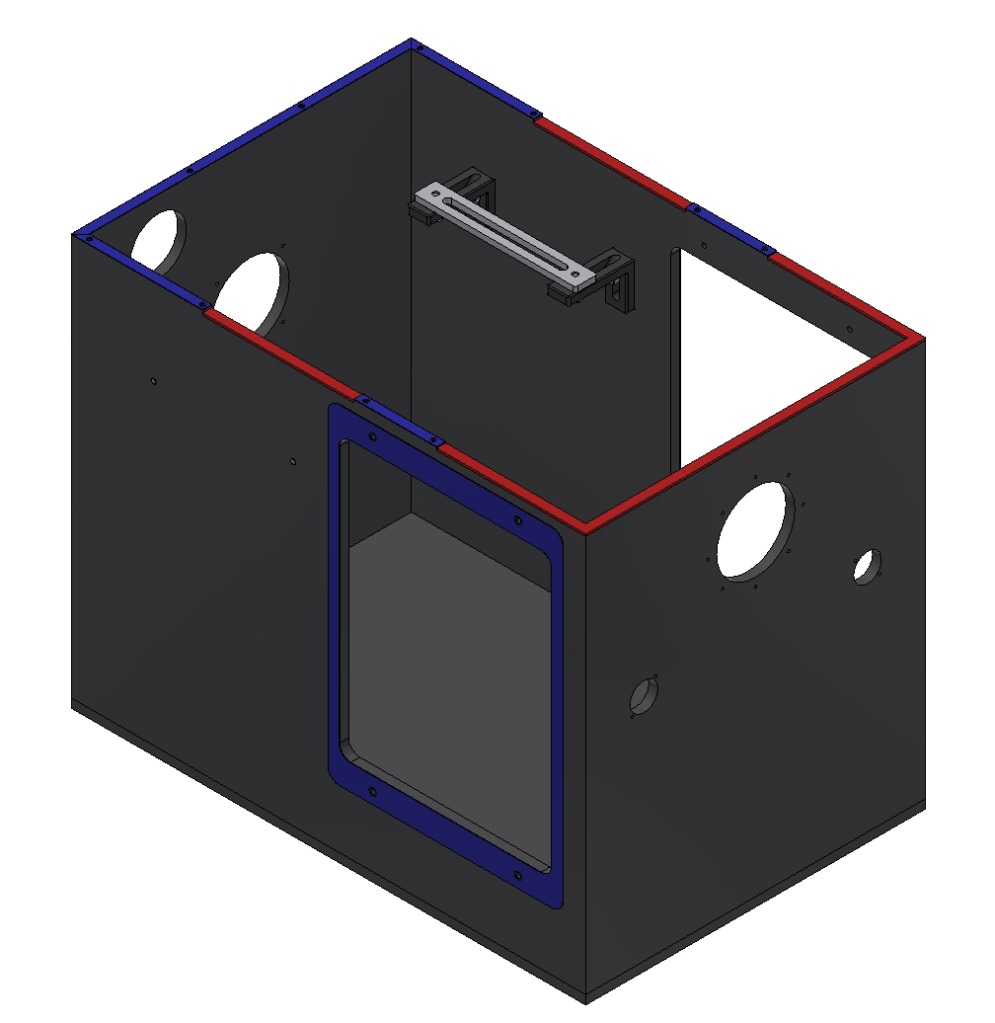
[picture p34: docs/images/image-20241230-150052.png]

   
Carefully the incubator is placed over the column and microscope onto the platform. Then the bottom covers M211 are fitted en bolted down. 
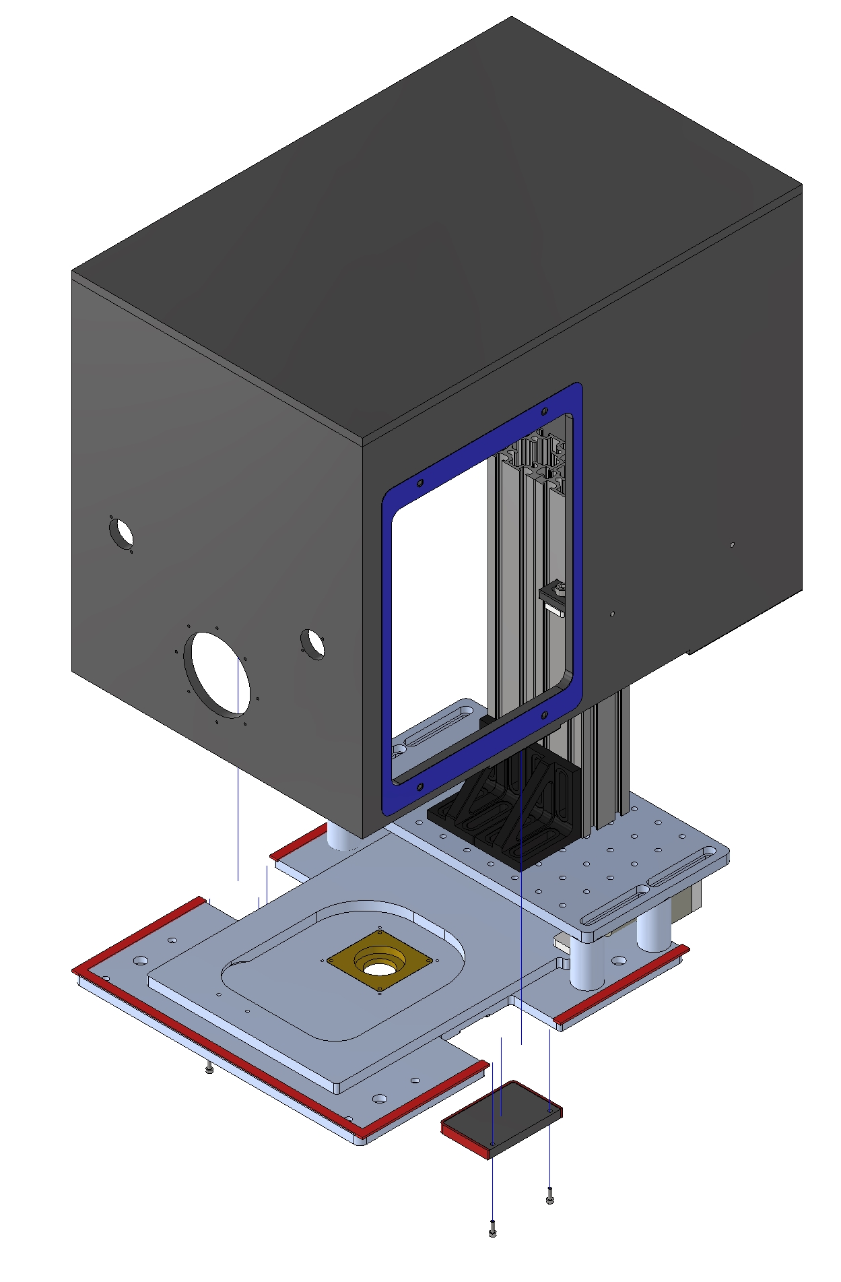
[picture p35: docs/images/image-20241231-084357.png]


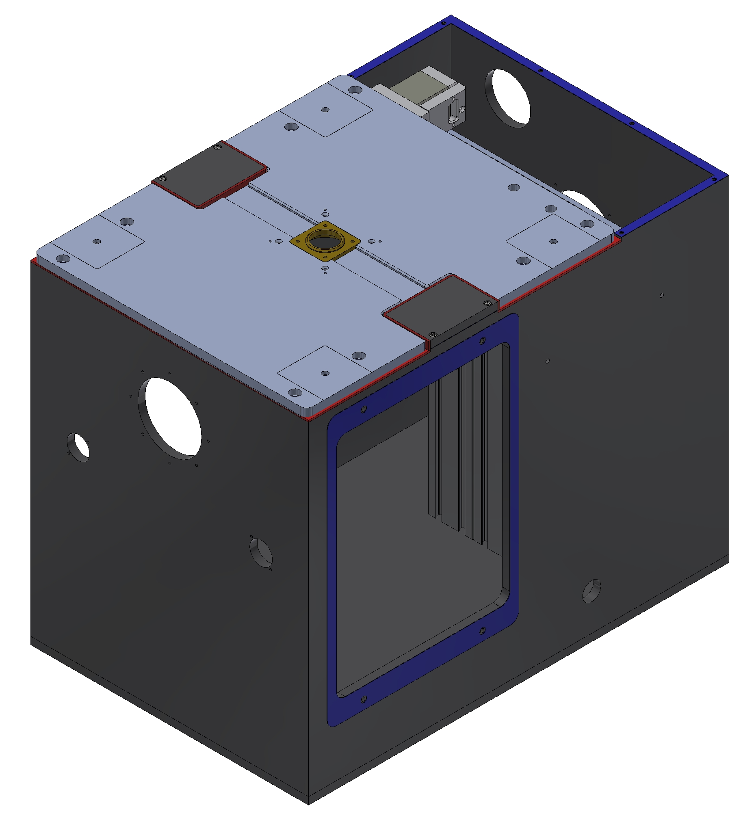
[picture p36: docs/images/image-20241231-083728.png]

After the bottom covers are mounted the two adjuster plates can be bolted to the platform. The bolts of the brackets can now be tightened. 
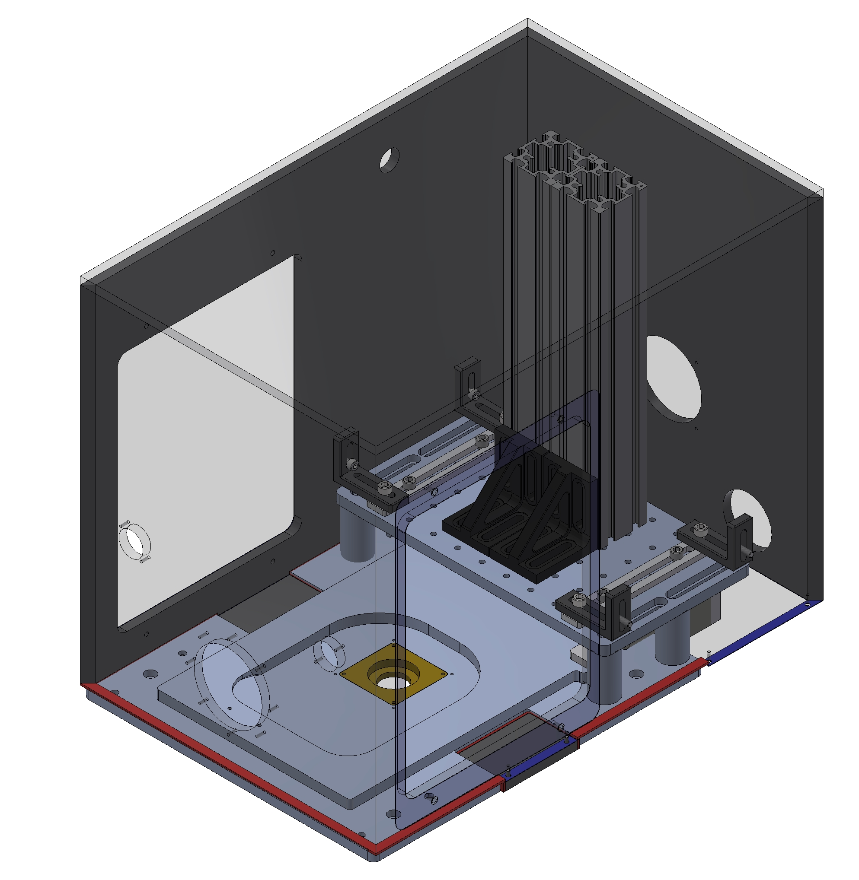
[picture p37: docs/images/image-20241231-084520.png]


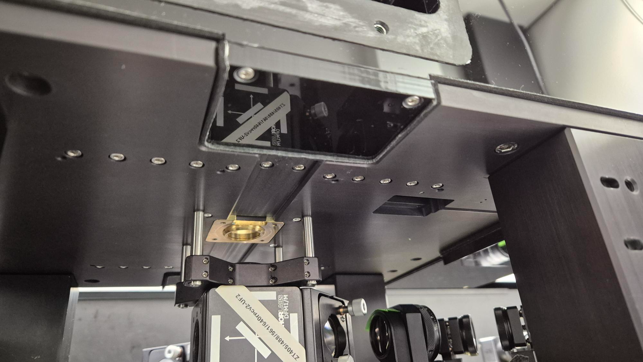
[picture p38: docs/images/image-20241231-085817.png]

    The last bottom cover can be mounted.
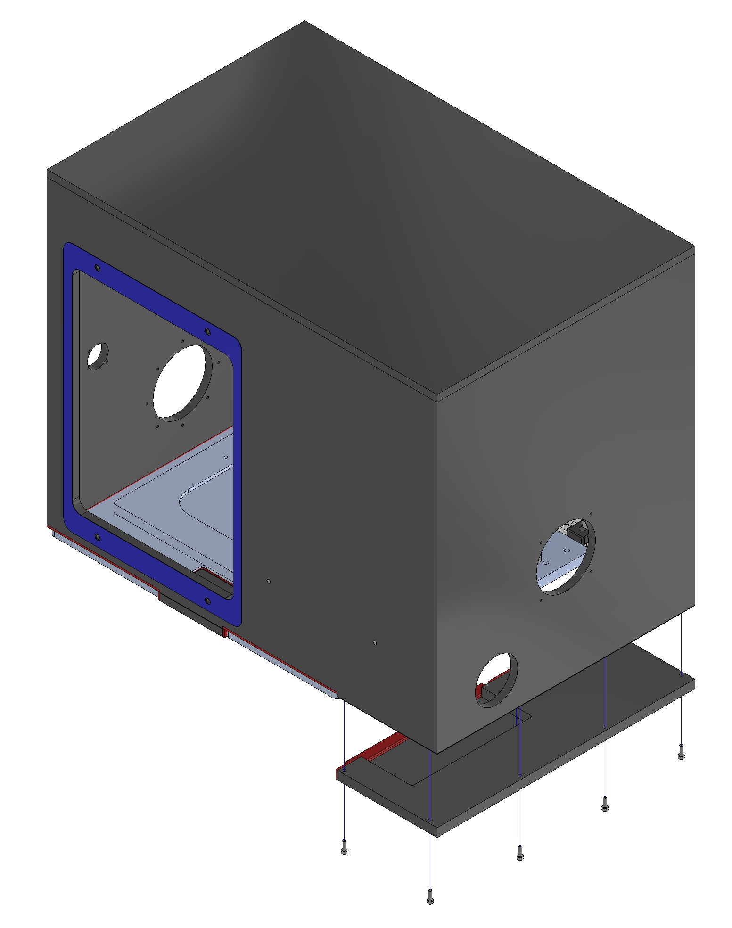
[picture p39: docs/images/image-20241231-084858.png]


The cables can be fitted through the cable glands and the cable glands can be place inside the incubator.
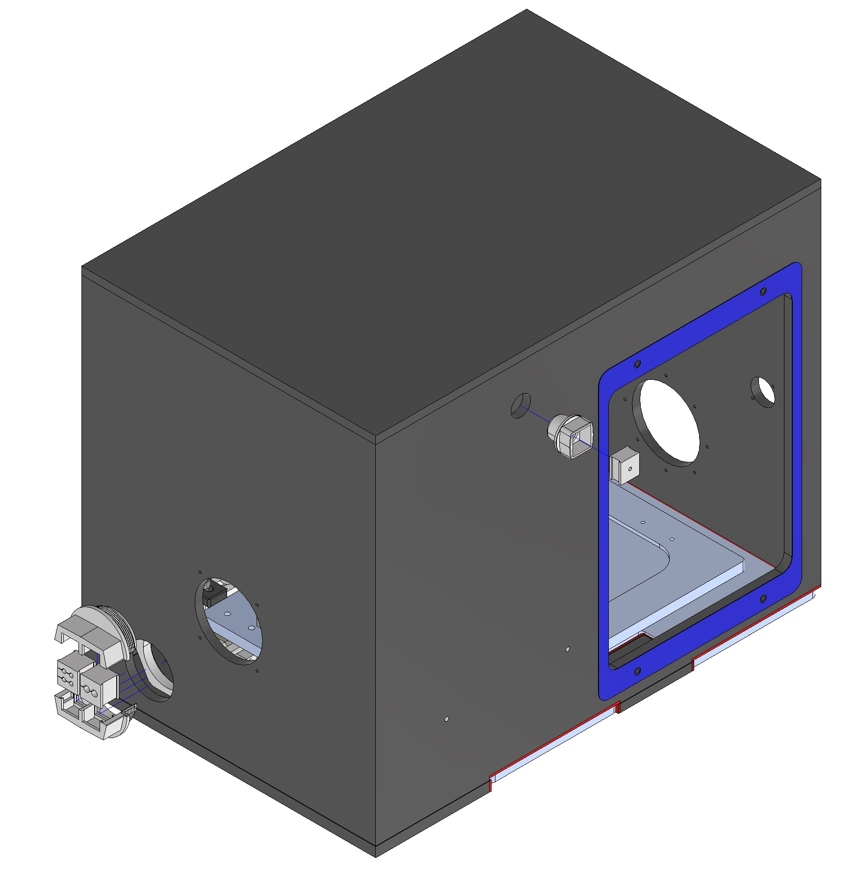
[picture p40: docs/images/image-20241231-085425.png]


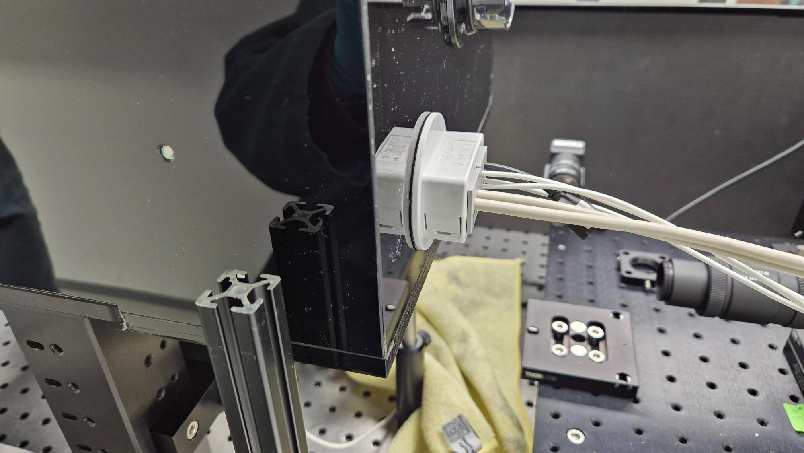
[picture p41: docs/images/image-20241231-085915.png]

The rest of the (air) connectors can be mounted to the incubator and the side covers can be placed.

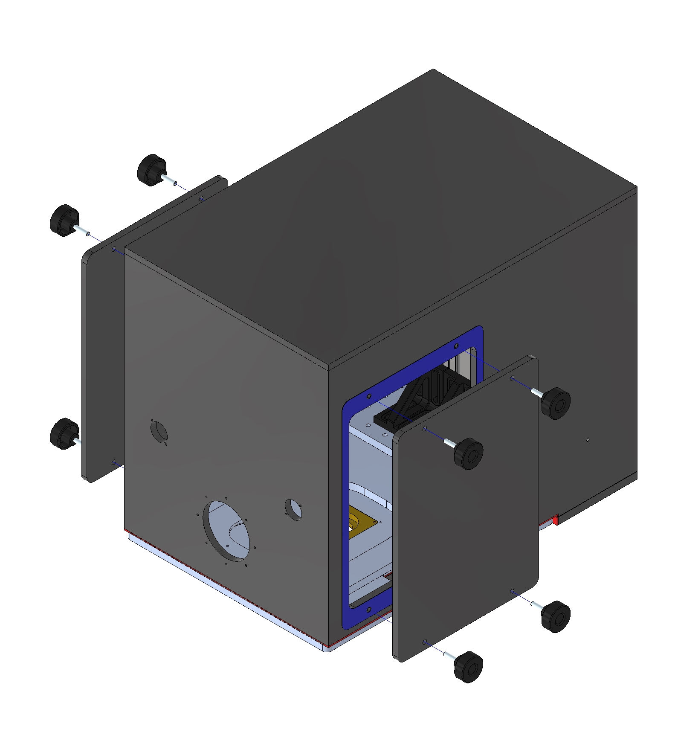
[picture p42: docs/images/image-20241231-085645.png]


# Implementation

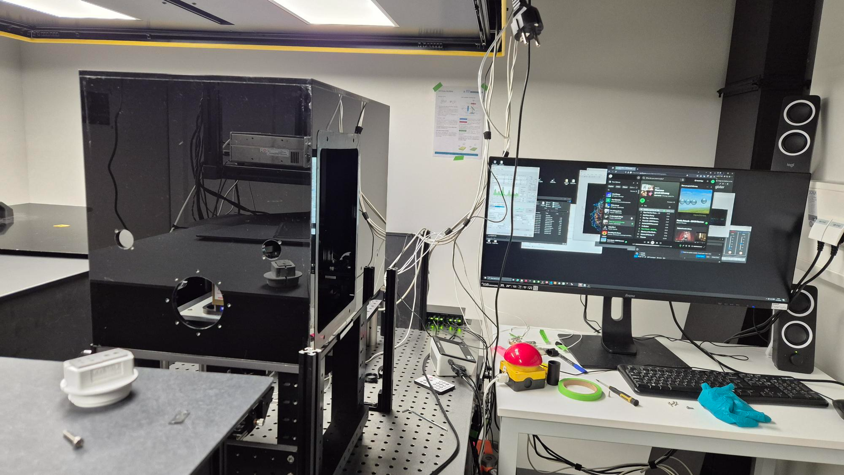
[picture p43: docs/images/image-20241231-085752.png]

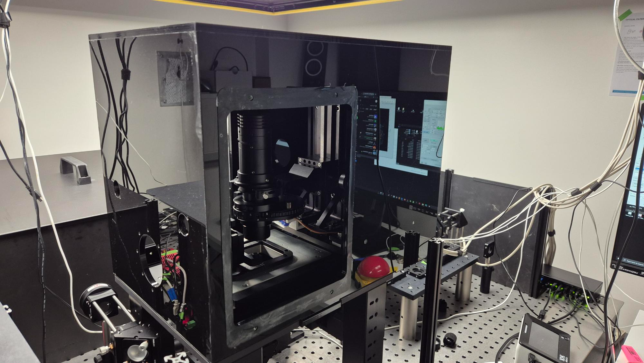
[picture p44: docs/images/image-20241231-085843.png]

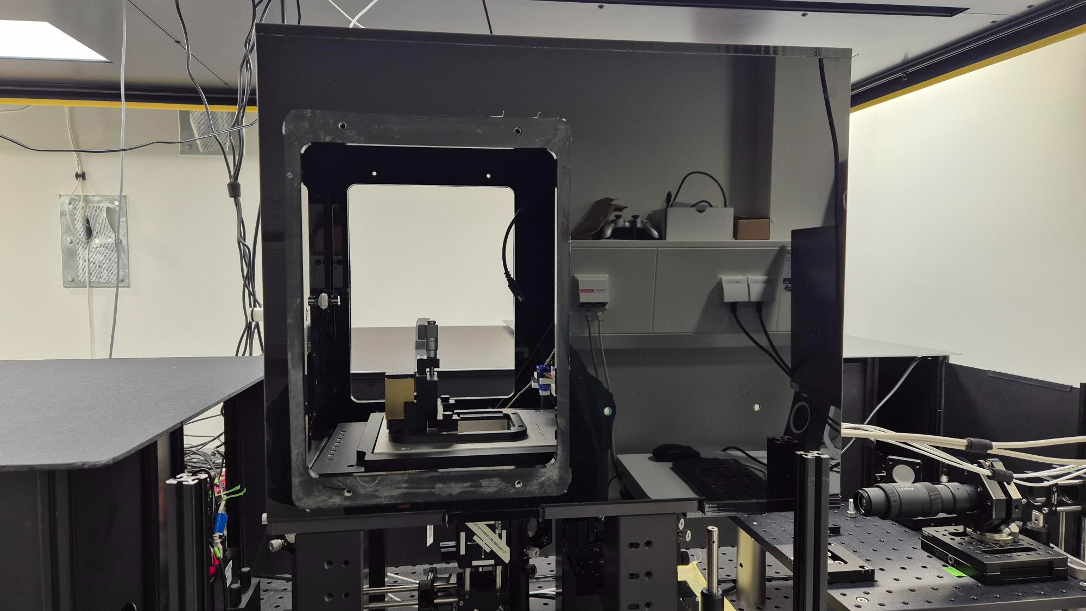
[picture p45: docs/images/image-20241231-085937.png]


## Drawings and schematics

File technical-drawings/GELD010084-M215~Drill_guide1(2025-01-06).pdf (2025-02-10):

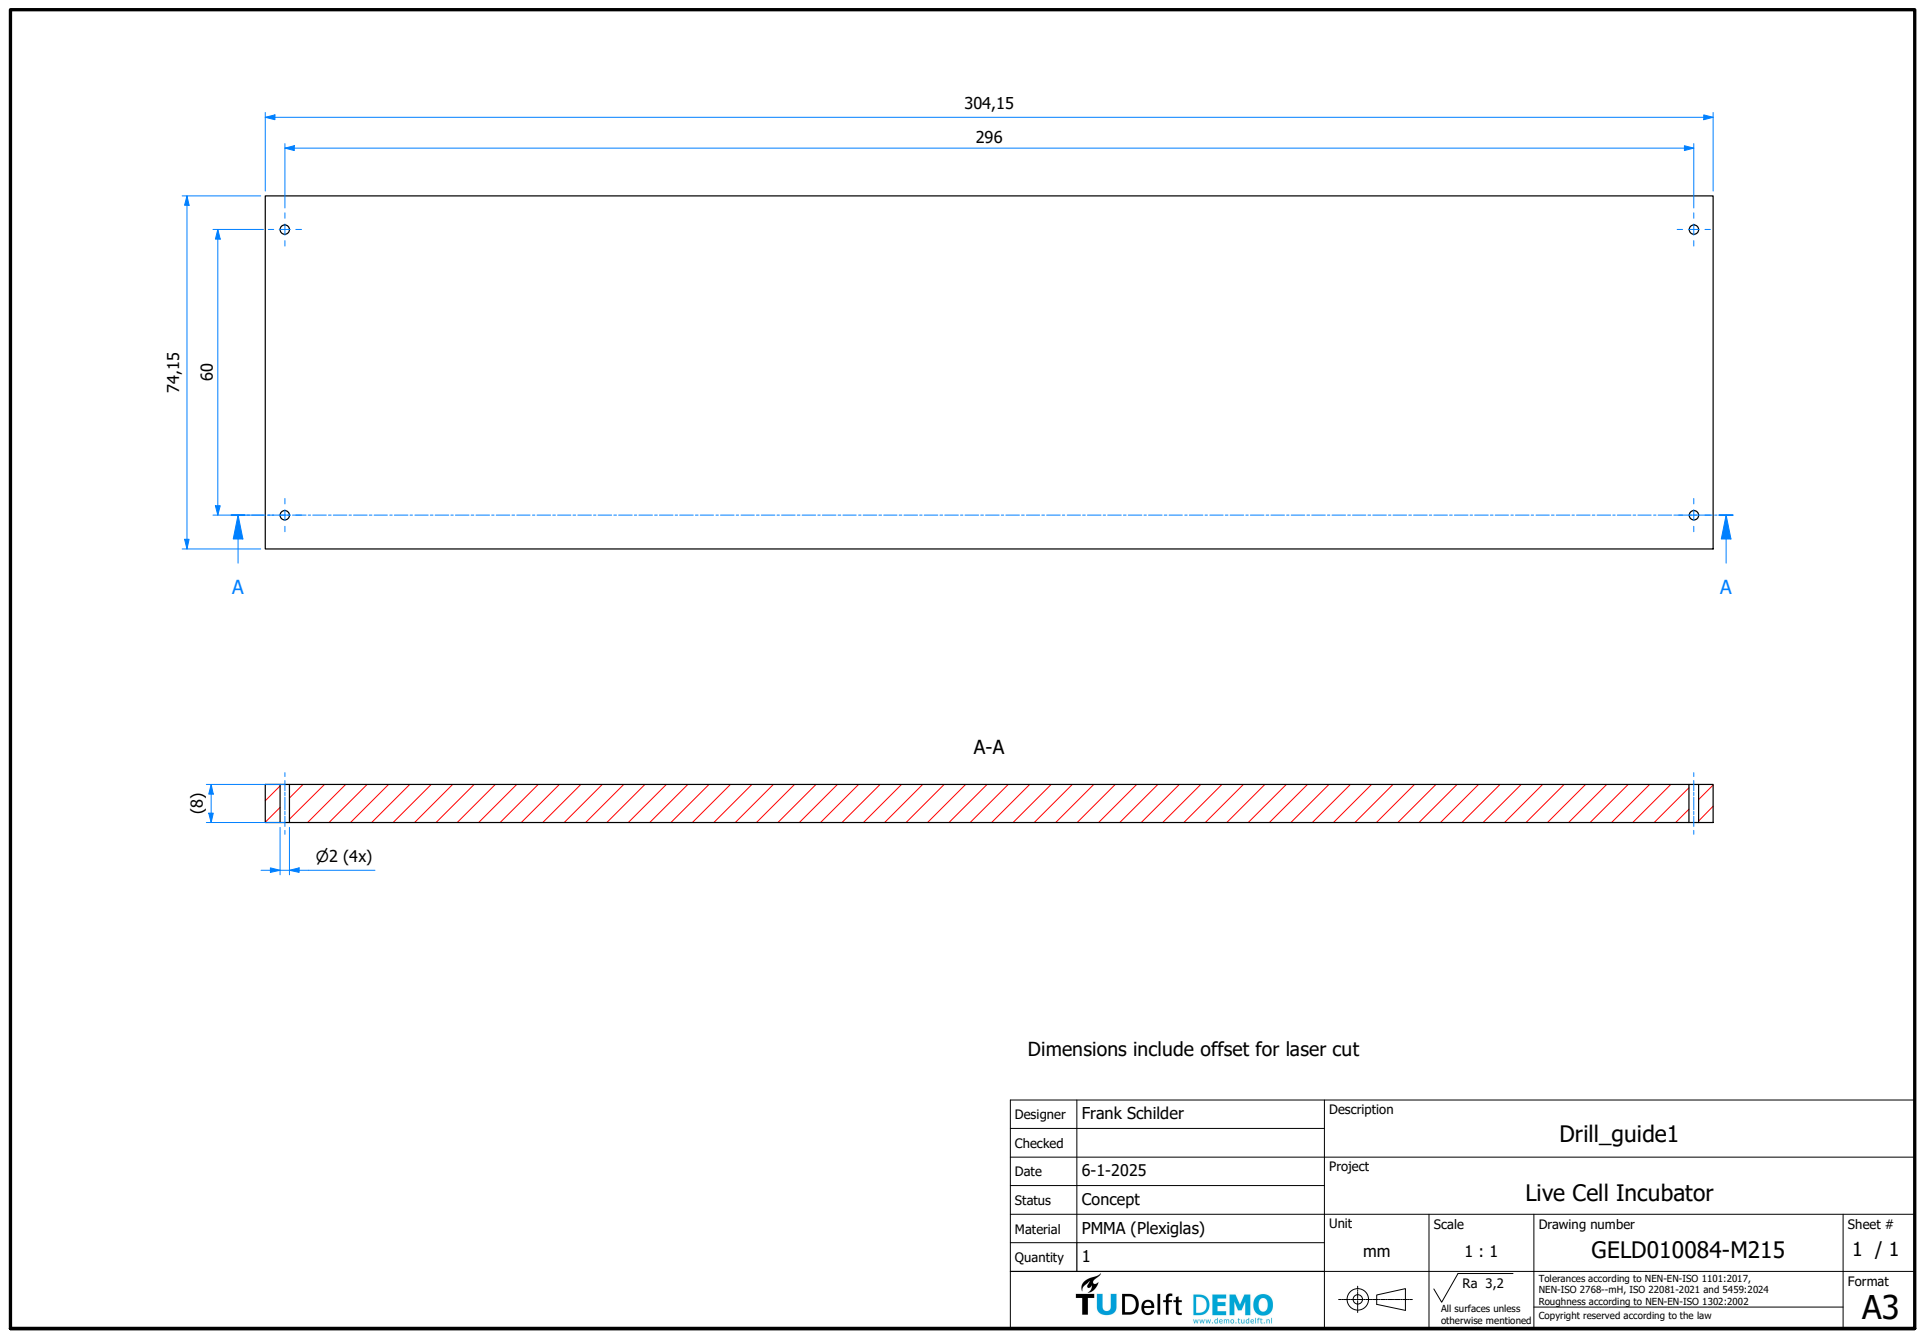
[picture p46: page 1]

Dimensions include offset for laser cut

Designer | Frank Schilder | Description Drill_guide1

Checked
Date | 6-1-2025 | Project Live Cell Incubator

Status | Concept

Material | PMMA (Plexiglas) | Unit mm | Scale 1 : 1 | Drawing number GELD010084-M215 | Sheet # 1 / 1

Quantity | 1

Ra 3,2 All surfaces unless otherwise mentioned | Tolerances according to NEN-EN-ISO 1101:2017, NEN-ISO 2768--mH, ISO 22081-2021 and 5459:2024 Roughness according to NEN-EN-ISO 1302:2002 | Format A3

Copyright reserved according to the law

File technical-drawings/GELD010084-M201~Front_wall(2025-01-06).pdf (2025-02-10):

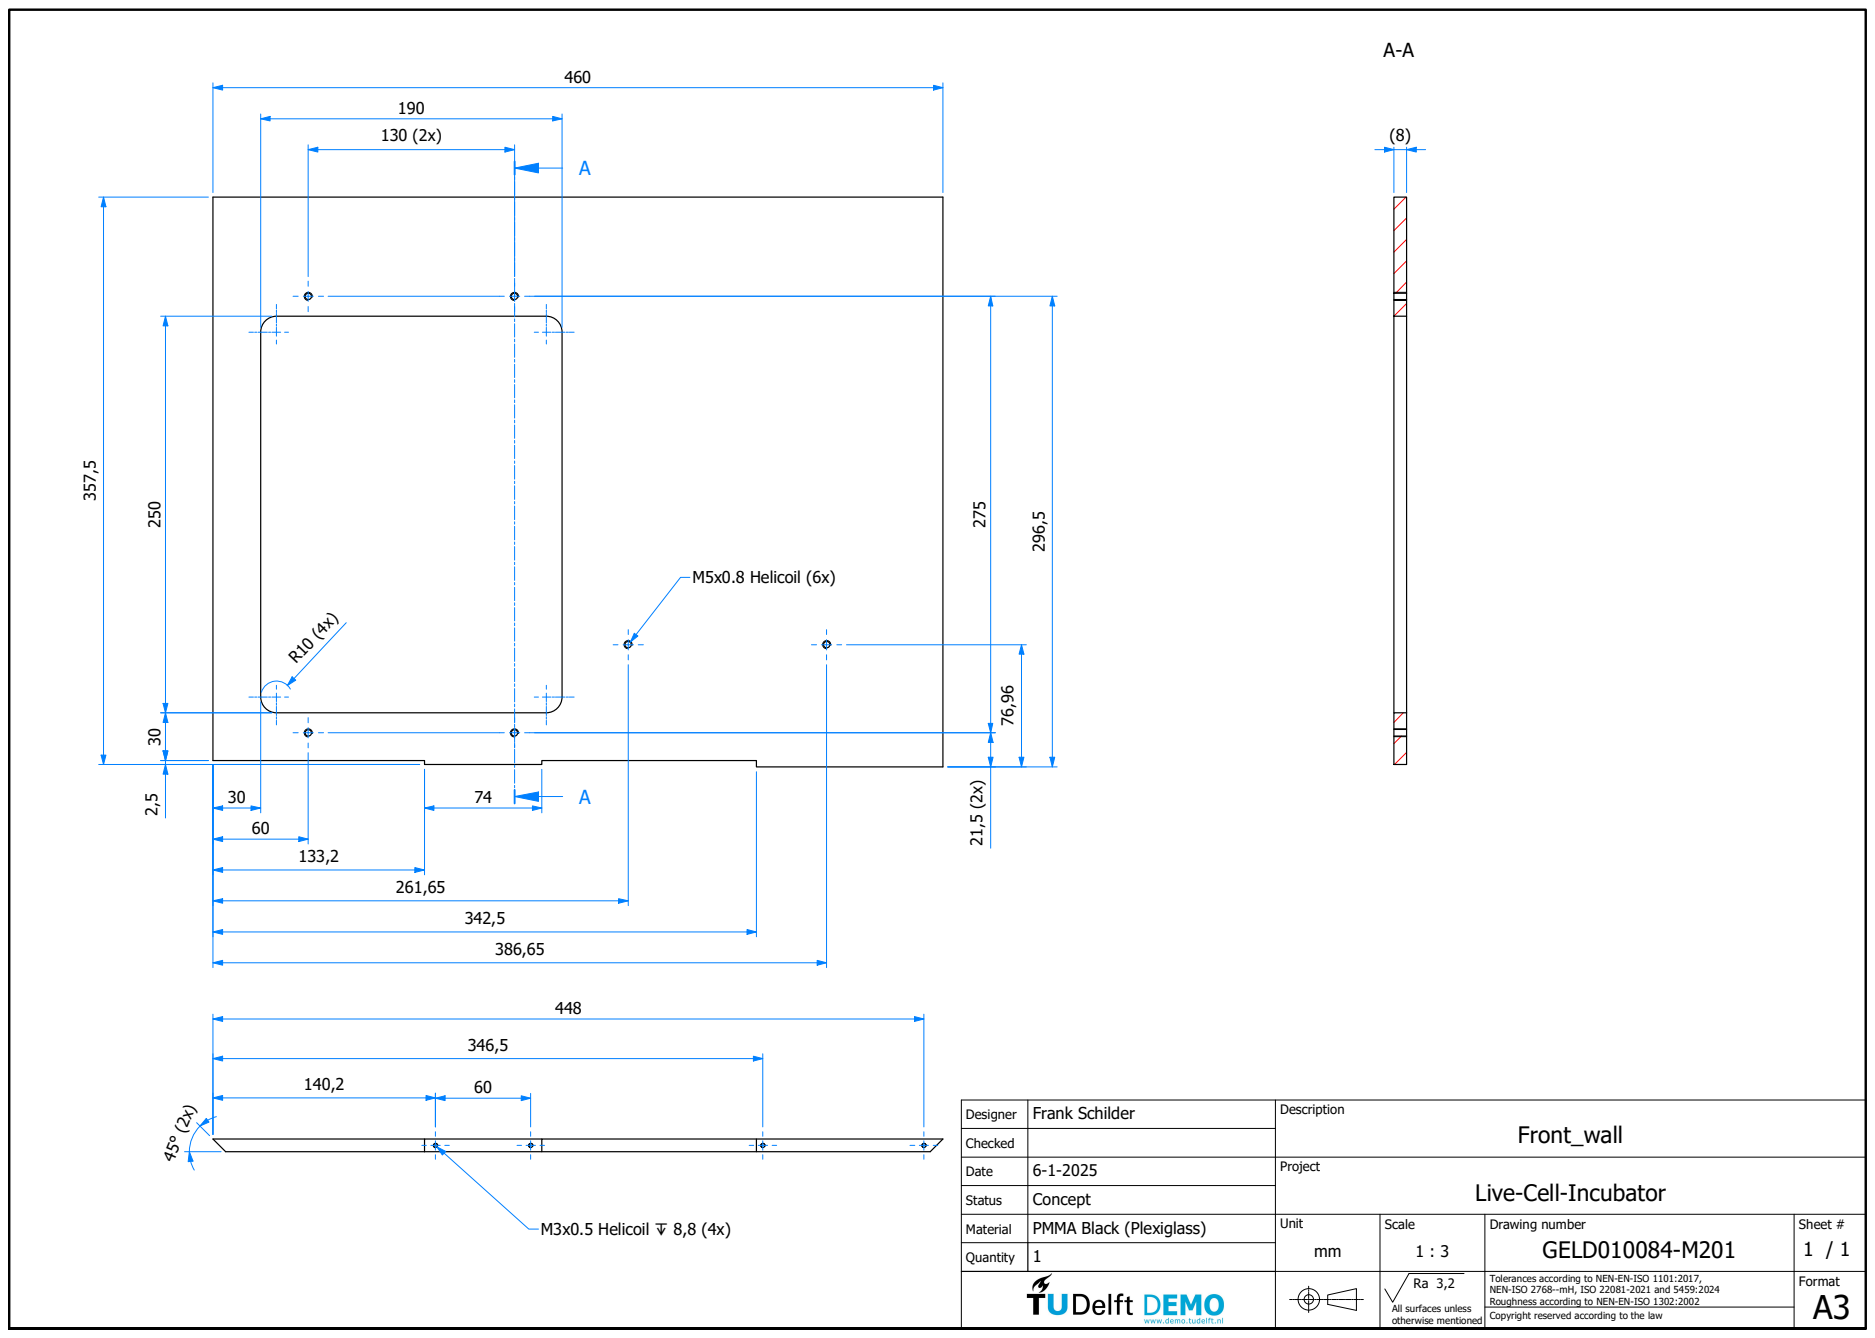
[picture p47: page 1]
M3x0.5 Helicoil ↧ 8,8 (4x); M5x0.8 Helicoil (6x)

Designer | Frank Schilder | Description Front_wall

Checked
Date | 6-1-2025 | Project Live-Cell-Incubator

Status | Concept

Material | PMMA Black (Plexiglass) | Unit mm | Scale 1 : 3 | Drawing number GELD010084-M201 | Sheet # 1 / 1

Quantity | 1

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

Copyright reserved according to the law

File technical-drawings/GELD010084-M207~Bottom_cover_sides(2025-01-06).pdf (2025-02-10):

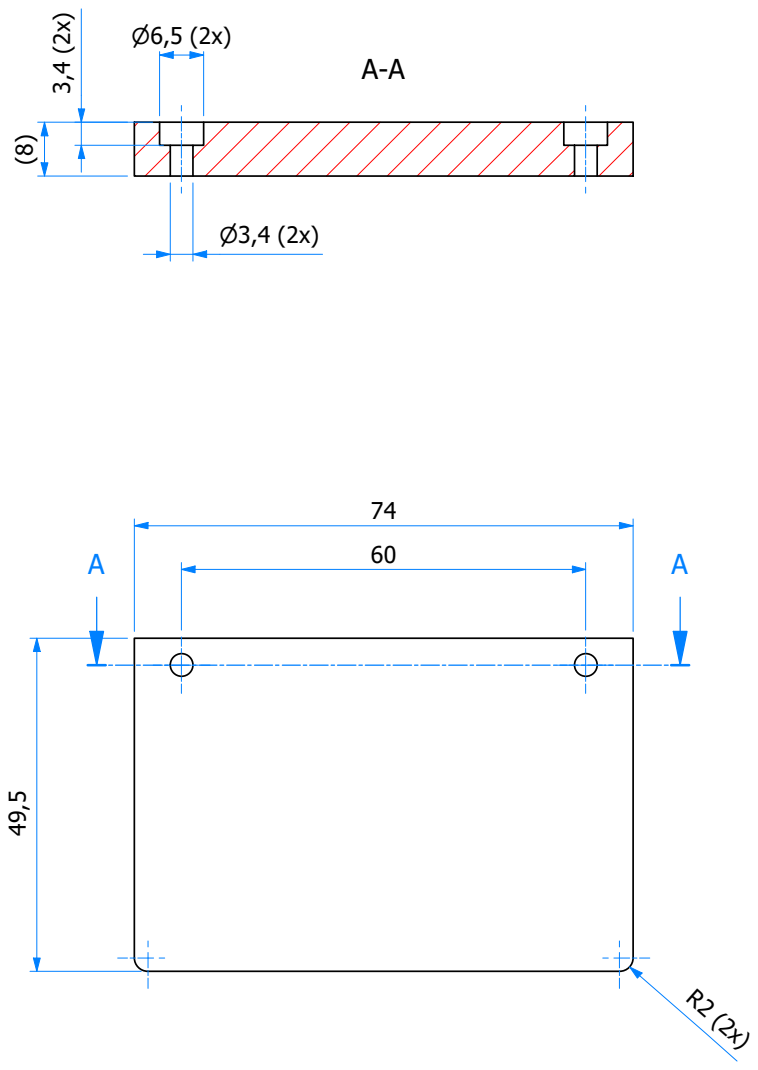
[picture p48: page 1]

Designer | Frank Schilder | Description Bottom_cover_sides

Checked
Date | 6-1-2025 | Project Live-Cell-Incubator

Status | Concept

Material | PMMA Black (Plexiglass) | Unit mm | Scale 1 : 1 | Drawing number GELD010084-M207 | Sheet # 1 / 1

Quantity | 2

Ra 3,2 All surfaces unless otherwise mentioned | Tolerances according to NEN-EN-ISO 1101:2017, NEN-ISO 2768--mH, ISO 22081-2021 and 5459:2024 Roughness according to NEN-EN-ISO 1302:2002 | Format A4

Copyright reserved according to the law
